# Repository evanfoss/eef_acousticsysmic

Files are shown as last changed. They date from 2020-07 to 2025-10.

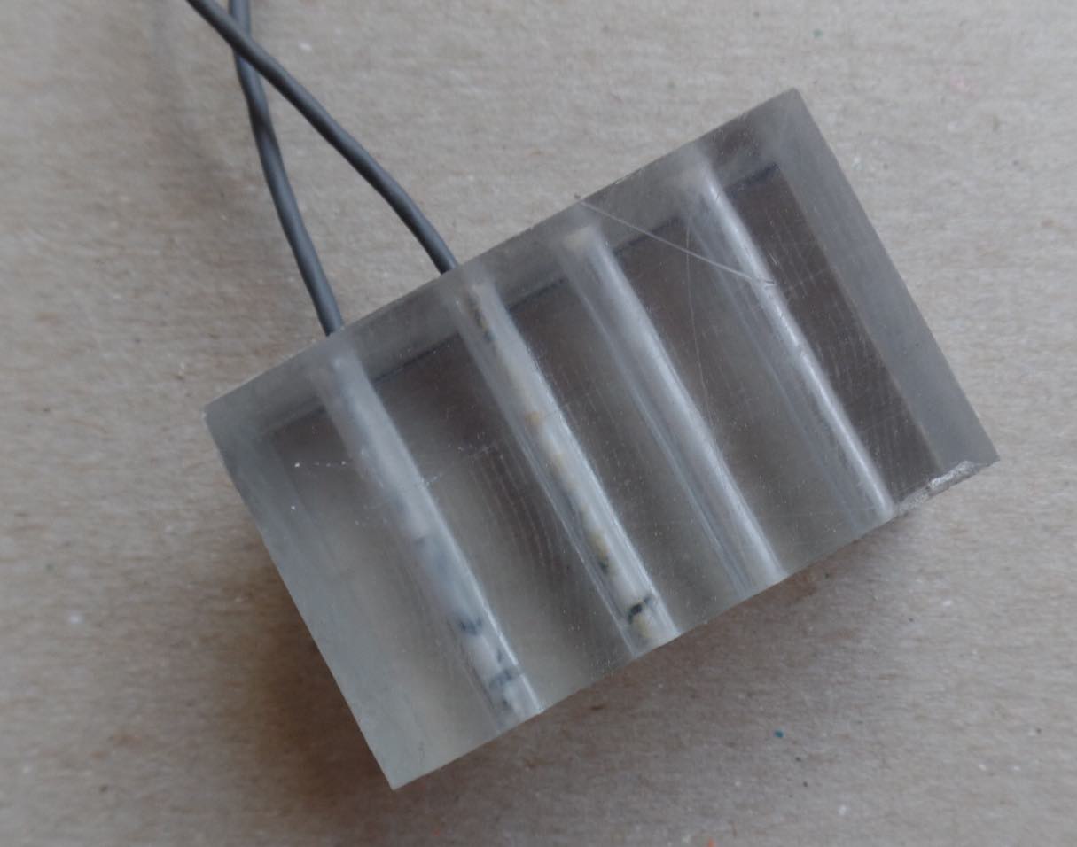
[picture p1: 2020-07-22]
fixturing/MicrophoneBufferCuringBlock_photo.jpg

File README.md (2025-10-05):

# EPL Acoustic System Microphone

Much like the Acoustic System Cable it might seem silly to make a whole project on github about putting a connector on a microphone. The thing is we optomized the process for this and we have different microphones so there are different variations of this project. The current version and the one we are first documenting here publicly is uses a Knowles FG microphone. Later we will include information on the EK series but this is not currently a priority as the microphones we used there are no longer manufactured.

This is my fork of the original project here: https://github.com/EPL-Engineering/epl_acousticsysmic

Tools (Suggested)
===================================

#11 scalpel and handle
Excelta 177-SE Scalpel Handle, Straight, SS, 5" OAL
I don't actually like this handle and if someone wants to recommend a better one that can be ordered in small quantity please let me know.

609IE211
Myco Scalpel Blade #11 Carbon Steel .015 pack of 100 blades

Tweezers 00-SA
I use a pair of Lindstrom tweezers with the corners rounded gentily with a fine grit sharpening stone.

"3rd Hand" Fixture

Diagonal cutters

Tubing Decurling Fixture

RTV Curing Fixture

Syringe with modified needle

BOM (Bill Of Matterials)
===================================

MFG #               MFG         Distributor         Distributor #               Description

RTV-748             Dow         McMaster Carr       74915A654                   Tube Paste -65°F to 350°F UL 94, 24hr set time

E-3603              Tygon       McMaster Carr       5155T14                     PVC Tubing for Chemicals 3/32" ID, 5/32" OD, 25 ft. Length

FG-23329-P07        Knowles     Mouser              721-FG-23329-P07            Omni-Directional Microphone with 1M long shielded cable

__________          Philmore    You Do It Elec.     ___                         5 position MiniDIN Male Cable Connector

Preassembly Process
===================================

We advise buying the tubing early and unwinding it. The tubing adopts a curl from being on coiled up that is an issue. To properly fit the inside of the acoustic system the tubing needs to not have the memory of this bend in it. To help remove this further we have designed a fixture which keeps the completed microphone assembly straight during the curing process. So please stop here, buy the tubing, make this fixture, and lay the tubing out. Obviously you should not leave anything to rest on top of the tubing as this will also distort it.

RTV should be preloaded into the syringe. This needs to be done without any air tripped in the syringe so the RTV stays fresh for as long as possible. The needle is removed and the plastic adapter it is made of is shaved down to widen it's hole and narrow it's width. Apply some RTV to the plunger before pressing it all the way in before using the syringe in reverse to pull RTV out of the tube.

Assembly Process
===================================

1. Cut the tubing to length.
2. Insert the tubing into the fixture.
3. Feed the cable for the microphone most of the way through the tubing leaving about 2 inches behind the microphone exposed.
4. Cut the heatshrink off the circumfrence of the microphone but not the cable. (this is not for the faint of heart)
5. Apply RTV to the 1/5" of microphone cable behind the microphone.
6. Pull the microphone back into the tubing until the front of the microphone is flat to the front of the tubing.
7. Wait until the RTV cures while doing steps 8 to .
8. Slide the outer miniDIN5 connector over the unterminated end of the cable with the narrow end facing the circuit board.
9. Strip the unterminated end of the multiconductor cable.
10. Solder the now exposed wires from the cable to the connectors pins. Be careful the connector melts easily.
11. Assemble the connectors internal shielding (the metal inner covers, and the plastic mid one. Do not slide the outer cover on.
12. Plug the connector into the mic. amp. and test that you soldered it correctly.
13. If it works continue to step 14. If it doesn't work disassemble the connector housing and return to step 10. If you already tried this once odds are you broke the microphone at step 4. Get a new microphoen and start over from step 1.
14. Now that you have something that works you can fill the partially assembled connector housing with RTV.
15. Push the outer housing over the inner layers you already assembled.
16. Let the whole thing sit for a day or two to cure and then retest.

Future Work
===================================

We are looking to mold or 3D print the tubing portion of the microphone so that it can fit around the heatshrink the manufacture applied.

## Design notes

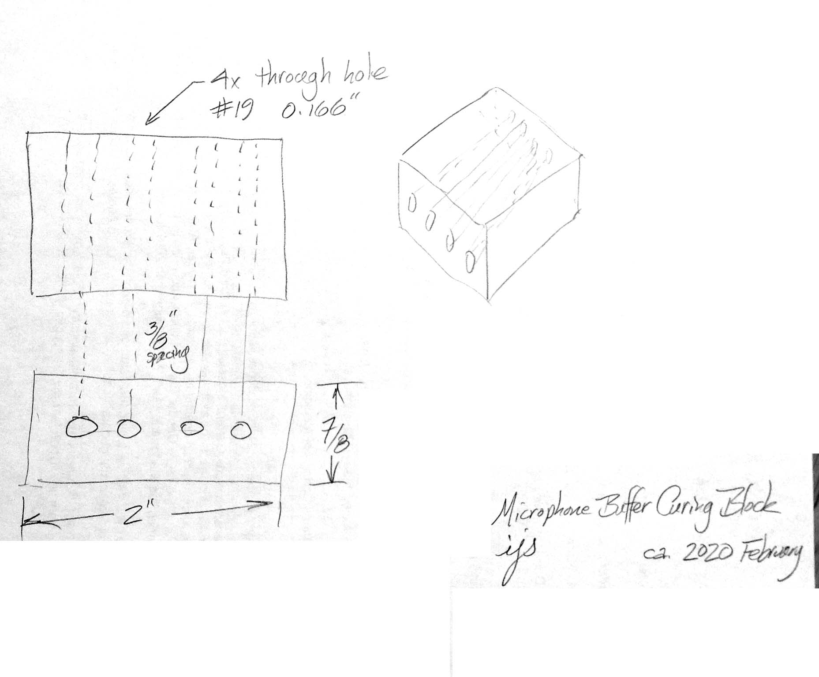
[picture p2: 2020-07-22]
fixturing/CuringBlockDrawing_pencil.JPG

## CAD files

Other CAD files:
fixturing/Tube holder.STEP

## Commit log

2020-06-23 add: more of the assembly process
2020-07-22 add: fixturing files from Ish
    [Tube holder.STEP]
